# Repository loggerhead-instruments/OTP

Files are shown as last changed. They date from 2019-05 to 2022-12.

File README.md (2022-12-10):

# OTP
OpenTag Ping is an open source acoustic pinger for fish and other animals.
OTP is unique in that it incorporates an accelerometer that can be used 
to determine when an animal is vocalizing, which then triggers a coded acoustic pulse.

## Altium
PCB files for OTP tags. Each PCB project will have a PDF document containing the schematic and PCB layout. The project outputs folder contain the Gerber files needed to have the PCB manufactured.

1. OTP: Simple design with ATmega328p and LIS2DS12 accelerometer. Not recommended.
2. OTP2: Improved transmitter circuit. Not recommended.
3. OTP3: Transmitter diode changed. Not recommended.
4. OTP4: PWM moved to PD3 to take advantage of built-in PWM.
5. OTP5: Smaller board designed to match lithium battery size. Recommended.
6. OTP6: Design for custom piezoceramic where lithium battery can be placed inside piezo cylinder. Also adds pressure and depth sensor. Recommended.

## Arduino
Arduino C code for programming OTP tags. 

The accelerometer uses SPI for high speed data transfer to lower power consumption.
The accelerometer can be configured for 3 channel operation or in a special magnitude mode where the magnitude of the 3 axes is calculated on the accelerometer. Magnitude mode reduces power consumption because it reduces how much time it takes to transmit and process the accelerometer data.

OTP4 firmware works on OTP4 and OTP5

## SpecSheets
The technical specification sheets for the components used in OTP tags

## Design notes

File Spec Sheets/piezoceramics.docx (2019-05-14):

57 kHz piezoceramic ring
(https://www.steminc.com/PZT/en/piezo-ceramic-cylinder-20x17x5mm-57-khz)

Part Number: SMC20D17H5
Piezoelectric ceramic cylinder with inner and outer surface electrode for radial mode vibration.
Piezo Material: SM111 (http://www.steminc.com/piezo/PZ_property.asp)
Dimensions: Ext. Diam. 20 x Int Diam 17 x Height 5.0mm
Resonant frequency fr: 57 KHz±2 KHz
Electromechanical coupling coefficient Kr: ≥35%
Dielectric Loss tg δ: =0.5%
Resonant impedance Zm: ≤12 Ω
Static capacitance Cs: 2400pF±15%@1kHz
Test Condition: 23±3 °C 40~70% R.H.
fr, Zm, Kr => Radial mode vibration
Cs tanδ => LCR meter at 1KHz 1Vrms

70 kHz piezoceramic ring
(https://www.steminc.com/PZT/en/annular-piezo-ceramic-70-khz)

Part Number: SMC1412T4412
Annular Piezoelectric Ceramic Ø14Ø12x4mm 70 KHz. Radial mode vibration
Piezo Material: SM411 (http://www.steminc.com/piezo/PZ_property.asp)
Dimensions: OD 14 x ID 12 x Th 4mm
Resonant frequency fr: 70 KHz ± 5%
Electromechanical coupling coefficient Kr: >30%
Dielectric Loss tg δ: <2%
Static capacitance Cs: 3900pF±20%
Test Condition: 23±3 °C 40~70% R.H.
fr, Zm, Kr => Radial mode vibration
Cs tanδ => LCR meter at 1KHz 1Vrms

127 kHz piezoceramic cylinder
(https://www.steminc.com/PZT/en/piezo-ceramic-cylinder-765x65x65mm-127-khz)

Part Number: SMC7565T65111
Piezoelectric Ceramic Cylinder. Radial mode vibration
Piezo Material: SM111 (http://www.steminc.com/piezo/PZ_property.asp)
Dimensions: 7.65x6.5x6.5mm
Resonant frequency fr: 127 KHz±5KHz
Electromechanical coupling coefficient Kr:
Dielectric Loss tg δ: 1.60
Resonant impedance Zm:
Static capacitance Cs: 4000pF±15%
Test Condition: 25±3 °C 40~70% R.H.
fr, Zm, Kr => Radial mode vibration
Cs tanδ => LCR meter at 1KHz 1Vrms

155 kHz piezoceramic cylinder
(https://www.steminc.com/PZT/en/piezo-ceramic-tube-o635o49x635mm-155-khz)

Part Number: SMC0604T6121
Piezoelectric Ceramic Cylinder. Radial mode vibration
Piezo Material: SM411 (http://www.steminc.com/piezo/PZ_property.asp)
Dimensions: OD 6.35 x ID 4.9 x Th 6.35mm
Resonant frequency fr: 155 KHz ± 5%
Dielectric Loss tg δ: <2%
Resonant Impedance: <150Ω
Static capacitance Cs: 2500pF±20%
Test Condition: 23±3 °C 40~70% R.H.
fr, Zm, Kr => Radial mode vibration
Cs tanδ => LCR meter at 1KHz 1Vrms

Inductance

Resonant frequency of LC circuit given by

f= 1/(2π√(L*C))

To calculate inductance for given frequency and capacitance (units of Hertz, Farads, Henrys):

L= 1/(2πf)^2 /C

Piezoceramic Frequency | Inductance | Resonance Frequency
57 kHz | 3.2485 mH
70 kHz | 1.3255 mH | 80 kHz @ 1000 uH
127 kHz | 0.3926 mH | 127.43 kHz @ 390 uH
155 kHz | 0.4111 mH | 161.2 kHz @ 390 uH

Two inductors in series:

127 kHz piezo: 390 uH

155 kHz piezo: 390 uH + 22 uH

For 4 MHz clock, it takes 1/4 microsecond per clock cycle. We can construct the following frequencies with an integer number of clock cycles per half-cycle (so n cycles high, n cycles low):

Frequency - Clock cycles per half cycle

250.0 kHz 8 clock cycles

222.2 kHz 9 clock cycles

200 kHz 10 clock cycles

181.8 kHz 11 clock cycles

166.7 kHz 12 clock cycles

And then 153.9 kHz, 142.9 kHz, 133.3 kHz, 125 kHz, 117.7 kHz, 111.1 kHz, 105.3 kHz, 100 kHz...

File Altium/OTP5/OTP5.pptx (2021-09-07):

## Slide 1

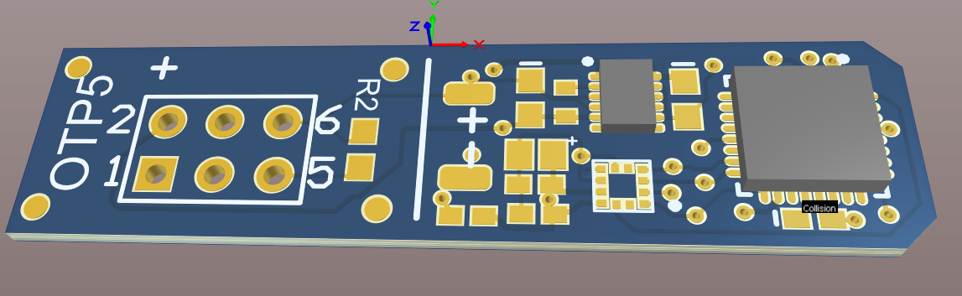
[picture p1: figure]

Battery connection

Microcontroller

Cut after programming

Accelerometer

LED

Magnetic Switch

Programming port

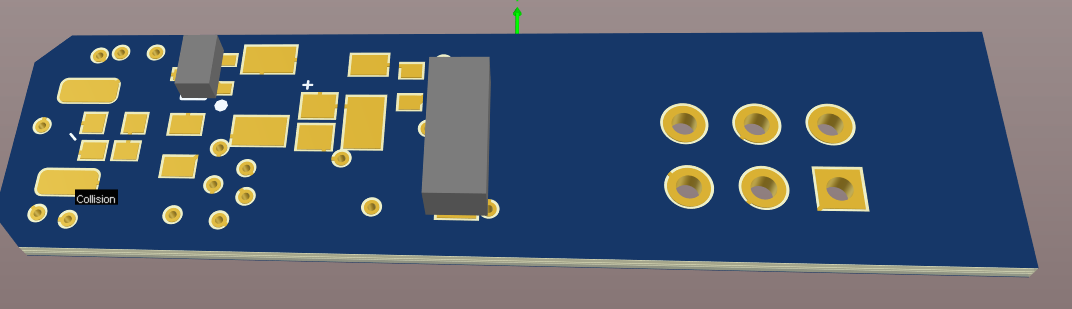
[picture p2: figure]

Piezo

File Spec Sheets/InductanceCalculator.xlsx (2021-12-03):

Frequency (Hz) | Capacitance (F) | Inductance (H) | mH | uH
57000 | 2.4e-09 | 0.003248473365 | 3.248473365 | 3248.473365
190000 | 1.65e-09 | 0.000425254695 | 0.425254695 | 425.254695
177000 | 6.35e-09 | 0.000127326853 | 0.127326853 | 127.326853
65000 | 8.5e-09 | 0.0007053336836 | 0.7053336836 | 705.3336836
30000 | 9e-09 | 0.003127197026 | 3.127197026 | 3127.197026
90000 | 5e-09 | 0.0006254394052 | 0.6254394052 | 625.4394052
127000 | 4e-09 | 0.0003926203719 | 0.3926203719 | 392.6203719
125000 | 3.5e-09 | 0.0004631825538 | 0.4631825538 | 463.1825538
66500 | 2.368e-08 | 0.0002418885297 | 0.2418885297 | 241.8885297 | custom piezo for 1/2AA battery

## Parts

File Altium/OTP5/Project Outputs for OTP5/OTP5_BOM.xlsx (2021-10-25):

Item # | Quantity | Designator | Mfg Part # | DigiKey | Comment | Description | Footprint | Type | Notes
1 | 2 | C1, C2 | C0603C106M7PAC7867 | ‎399-17780-1-ND‎ (https://www.digikey.com/product-detail/en/L0603B470KPWFT/399-17780-1-ND/8601443?itemSeq=376672183) | 10uF | Ceramic Chip Capacitor - Standard | 0603 | smt
2 | 3 | C3, C4, C6 | CC0402KPX7R8BB104 | 13-CC0402KPX7R8BB104CT-ND | 0.1uF | Ceramic Chip Capacitor - X5R, 10% | 0402 | smt
3 | 1 | C5 | F920J106MPA | 478-8115-1-ND | 10uF | Tantalum Capacitor, 20%, 6.3V or better | Tant0805 | smt
4 | 1 | C7 | F921A105MPA | 478-8122-1-ND | 47uF | Tantalum Capacitor, 20%, 6.3V or better | Tant0805 | smt
5 | 1 | D1 | HSMH-C190 | 516-1420-1-ND | LED_0603 | Red LED | Diode0603 | smt
6 | 1 | D3 | DFLS130L-7 | DFLS130LDIDKR-ND | Shottky | Schottky diode 30V 1A | DFLS130 | smt
7 | 1 | L1 | CBC3225T101MR | 587-1628-1-ND | 100uH | Fixed inductor | Inductor_NLV32T | smt
8 | 1 | L2 | MLZ1608A2R2WTD25 | 445-MLZ1608A2R2WTD25CT-ND | 2.2uH | Fixed inductor | Inductor KLZ1608AHR | smt
9 | 1 | L3 | L0603B470KPWFT | 399-17780-1-ND | 47uH | Fixed inductor | Inductor KLZ1608AHR | smt
10 | 1 | L4 | MLF2012C270KT000 | 445-1064-1-ND | 27uH | Fixed inductor | Inductor MLZ2012M220WT000 | smt
11 | 1 | Q1 | PMF250XNE | 1727-2693-1-ND | PMF250XN,115 | N-Channel Trench MOSFET, 30 V, 0.9 A, -55 to 150 degC, 3-Pin SOT323, Tape and Reel | NXP-SOT323_N | smt
12 | 1 | R1 | ERJ-PA2J103X | P17199CT-ND | 10k | ERJ-3EKF1002V 10k 5% 0603 | 2-0402 | smt
13 | 0 | R2 |  |  | omit |  | 3-0603 | DNS
14 | 1 | R3 | ERJ-2GEJ331X | P330JCT-ND | 330 | Precision Thick Film Chip Resistor, 10 Ohm to 1M Ohm Range, 1% and 0.5% Tolerance, 0402 Size, 0.063 W | 2-0402 | smt
15 | 1 | S1 | MK24-B-3-OE | 374-1137-1-ND | Reed_MK24 | SWITCH REED SPST-NC 300MA 30V | Reed MK24-B-3 | smt | Either orientation is OK. All boards should have same orientation
16 | 1 | U1 | ATMEGA328P-MU | ATMEGA328P-MU-ND | ATmega328p | 8-Bit AVR Microcontroller with 8K Bytes of In-System Programmable Flash Memory | 32M1-A_M | smt
17 | 1 | U2 | TPS62740DSSR | 296-39459-6-ND | TPS62740 | 1.8V regulator | TPS6274x | smt
18 | 1 | U3 | LIS2DS12TR | 497-16261-6-ND | LIS2DS12 | Accelerometer | LGA-12 | smt
Loggerhead Instruments
David Mann
941-266-2908
dmann@loggerhead.com

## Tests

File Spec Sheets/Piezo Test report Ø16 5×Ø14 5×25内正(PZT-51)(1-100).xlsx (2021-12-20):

Dimension： OD16.5*ID14.5*25mm |  |  |  | Material： PZT-51
Num | Radial Resonate Frequency | Anti-Resonate Frequency | Frequency Bandwidth | Status Capacitance | Dielectric Loss
 | Fs(KHz) | Fp(KHz) | Fp-Fs(Hz) | C(pf) | tg△(%)
1 | 69.89 | 88 | 18112 | 21540 | 1.8
2 | 70.14 | 88.32 | 18176 | 21340 | 1.8
3 | 69.95 | 88.48 | 18528 | 21530 | 1.8
4 | 70.14 | 87.36 | 17216 | 23680 | 1.8
5 | 70.27 | 87.84 | 17568 | 22430 | 1.8
6 | 70.21 | 88 | 17792 | 22660 | 1.8
7 | 69.84 | 88 | 18160 | 21560 | 1.8
8 | 70.02 | 88.16 | 18144 | 21690 | 1.8
9 | 69.76 | 88 | 18240 | 22010 | 1.8
10 | 69.68 | 88.16 | 18480 | 22340 | 1.8
11 | 70.21 | 88.4 | 18192 | 21090 | 1.8
12 | 70.14 | 87.36 | 17216 | 23360 | 1.8
13 | 69.95 | 88.4 | 18448 | 21330 | 1.8
14 | 70.08 | 88.16 | 18080 | 21110 | 1.8
15 | 70.02 | 88.24 | 18224 | 21730 | 1.8
16 | 70.08 | 88.32 | 18240 | 21100 | 1.8
17 | 69.68 | 87.84 | 18160 | 21990 | 1.8
18 | 69.92 | 88 | 18080 | 22650 | 1.8
19 | 70.08 | 88.64 | 18560 | 21500 | 1.8
20 | 69.76 | 88 | 18240 | 21880 | 1.8
21 | 70.21 | 87.36 | 17152 | 23060 | 1.8
22 | 69.76 | 88.16 | 18400 | 21470 | 1.8
23 | 69.76 | 88.16 | 18400 | 21330 | 1.8
24 | 69.68 | 88.32 | 18640 | 21500 | 1.8
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

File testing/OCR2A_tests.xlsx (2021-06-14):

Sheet: Prescaler=1
OCR2A | Frequency | kHz | peak-peak (V) | dB-peak' | Freq (kHz) | Notes | Setup
21 | 181818.1818 | 181.8181818 | 56 | 180.9431606 |  | bad | Reson about 2 inches from piezo
22 | 173913.0435 | 173.9130435 | 56 | 180.9431606 |  | bad | 4 MHz after prescalar
23 | 166666.6667 | 166.6666667 | 192 | 191.6454247 | 163 |  | Frequency measured from oscilloscope
24 | 160000 | 160 | 304 | 195.6368718 | 145 | nice
25 | 153846.1538 | 153.8461538 | 512 | 200.1647993 | 143 | nicer
26 | 148148.1481 | 148.1481481 | 252 | 194.0074109 | 137
27 | 142857.1429 | 142.8571429 | 528 | 200.4320785 | 140 | good
28 | 137931.0345 | 137.9310345 | 832 | 204.3818666 | 113 | excellent
29 | 133333.3333 | 133.3333333 | 320 | 196.0823997 | 130
30 | 129032.2581 | 129.0322581 | 296 | 195.4052343 | 116
31 | 125000 | 125 | 668 | 202.4749293 | 122 | v good
32 | 121212.1212 | 121.2121212 | 804 | 204.0845211 | 118 | excellent
33 | 117647.0588 | 117.6470588 | 376 | 197.483157 | 115
34 | 114285.7143 | 114.2857143 | 284 | 195.0457669 | 108
35 | 111111.1111 | 111.1111111 | 484 | 199.6763073 | 108
36 | 108108.1081 | 108.1081081 | 188 | 191.4625571 | 106
37 | 105263.1579 | 105.2631579 | 520 | 200.299467 | 103
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

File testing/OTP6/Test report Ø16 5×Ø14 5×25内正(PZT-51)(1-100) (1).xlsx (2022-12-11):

Dimension： OD16.5*ID14.5*25mm |  |  |  | Material： PZT-51
Num | Radial Resonate Frequency | Anti-Resonate Frequency | Frequency Bandwidth | Status Capacitance | Dielectric Loss
 | Fs(KHz) | Fp(KHz) | Fp-Fs(Hz) | C(pf) | tg△(%)
1 | 69.89 | 88 | 18112 | 21540 | 1.8
2 | 70.14 | 88.32 | 18176 | 21340 | 1.8
3 | 69.95 | 88.48 | 18528 | 21530 | 1.8
4 | 70.14 | 87.36 | 17216 | 23680 | 1.8
5 | 70.27 | 87.84 | 17568 | 22430 | 1.8
6 | 70.21 | 88 | 17792 | 22660 | 1.8
7 | 69.84 | 88 | 18160 | 21560 | 1.8
8 | 70.02 | 88.16 | 18144 | 21690 | 1.8
9 | 69.76 | 88 | 18240 | 22010 | 1.8
10 | 69.68 | 88.16 | 18480 | 22340 | 1.8
11 | 70.21 | 88.4 | 18192 | 21090 | 1.8
12 | 70.14 | 87.36 | 17216 | 23360 | 1.8
13 | 69.95 | 88.4 | 18448 | 21330 | 1.8
14 | 70.08 | 88.16 | 18080 | 21110 | 1.8
15 | 70.02 | 88.24 | 18224 | 21730 | 1.8
16 | 70.08 | 88.32 | 18240 | 21100 | 1.8
17 | 69.68 | 87.84 | 18160 | 21990 | 1.8
18 | 69.92 | 88 | 18080 | 22650 | 1.8
19 | 70.08 | 88.64 | 18560 | 21500 | 1.8
20 | 69.76 | 88 | 18240 | 21880 | 1.8
21 | 70.21 | 87.36 | 17152 | 23060 | 1.8
22 | 69.76 | 88.16 | 18400 | 21470 | 1.8
23 | 69.76 | 88.16 | 18400 | 21330 | 1.8
24 | 69.68 | 88.32 | 18640 | 21500 | 1.8
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

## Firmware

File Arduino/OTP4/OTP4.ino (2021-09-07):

// OpenTag Ping 
// 

// Fuses
// Extended: FF
// High: D9
// Low: E2

// baseline current no transmission: 295 uA
// baseline current  (transmitting single pulse): 330 uA
// 256 ms for pulse, 1.87 mA

#include <SPI.h>    // arduino pro/pro mini, AtMega328p 3.3V 8 MHz
#include <avr/io.h>
#include <avr/sleep.h>
#include <avr/power.h>
#include <util/delay.h>
#include <prescaler.h>
#include <avr/wdt.h>

// ID Codes
// boolean tagID[8] = {1,1,1,1,0,0,0,0};  // tag 1
boolean tagID[8] = {0,0,0,0,1,1,1,1};  // tag 2
// boolean tagID[8] = {1,1,1,1,1,1,1,1};  // tag 3
// boolean tagID[8] = {0,0,0,0,0,0,0,0};  // tag 4
// boolean tagID[8] = {1,0,0,1,1,1,0,0};  // tag 5
// boolean tagID[8] = {1,1,1,0,0,0,1,1};  // tag 6

uint8_t pulse = 0; // index into tagID - we can also use register counting with timer1 and pin5: https://forum.arduino.cc/index.php?topic=494744.0

// Detector settings
#define DET_THRESHOLD 450 // Detection threshold - 110 [mg] / 0.2441 [mg/sample]
#define DET_CRIT 8        // Critical number of detected blocks
#define DET_BLOCK 8       // Number of accelerometer samples per block

// OLD DETECTOR SETTINGS - TO DELETE
int16_t threshold = 100; // threshold for detecting signal
uint16_t thresholdCount = 100; // n values need to exceed threshold in one buffer to trigger
uint16_t bufCounter = 0; // counter for number of buffers processed. Used to control signal of tagID regardless of whether sound detected

// calculate number of bits based on tagID
//uint8_t NBIT = *(&tagID + 1) - tagID;
#define NBIT (*(&tagID + 1) - tagID)


#define LED A2
#define PWMPIN 3
#define DATAOUT 11      //MOSI
#define DATAIN 12       //MISO
#define SPICLOCK 13      //sck
#define chipSelectPinAccel 9  
#define INT1 2


// defines for setting and clearing register bits - check if we use these, switch to _BV
#ifndef cbi
#define cbi(sfr, bit) (_SFR_BYTE(sfr) &= ~_BV(bit))
#endif
#ifndef sbi
#define sbi(sfr, bit) (_SFR_BYTE(sfr) |= _BV(bit))
#endif

// default number of channels and sample rate
// can be changed by setup.txt file
// change lis2SpiFifoRead if choosing sample rate combo of 12 bit acc data
int nchan = 1;
int srate = 800;
int accelScale = 2;

// when storing magnitude of acceleraton watermark threshold are represented by 1Lsb = 3 samples
// max buffer is 256 sets of 3-axis data
#define FIFO_WATERMARK (0x80) // samples 0x0C=12 0x24=36; 0x2A=42; 0x80 = 128
#define bufLength 384 // samples: 3x watermark
int16_t accel[bufLength]; // hold up to this many samples


void setup() {
  delay(2000);
  setClockPrescaler(1); //slow down clock to run at 1.8V; makes 4 MHz clock
  pinMode(PWMPIN, OUTPUT); // output pin for OCR2B
  pinMode(LED, OUTPUT);
  digitalWrite(LED, HIGH);
  
  // initalize the  data ready and chip select pins:
  pinMode(chipSelectPinAccel, OUTPUT);
  digitalWrite(chipSelectPinAccel, HIGH);
  pinMode(SPICLOCK, OUTPUT);
  pinMode(DATAOUT, OUTPUT);
  pinMode(DATAIN, INPUT);

  // initialize watchdog timer. Remember to continuously re-initialize
  wdt_enable(WDTO_8S); // watchdog timer with 8 s timeout

  SPI.begin();
  SPI.beginTransaction(SPISettings(2000000, MSBFIRST, SPI_MODE0)); // with breadboard, speeds higher than 1MHz fail

  int testResponse = lis2SpiTestResponse();
  while (testResponse != 67) {
    delay(100);
    digitalWrite(LED, HIGH);
    delay(100);
    digitalWrite(LED, LOW);
    testResponse = lis2SpiTestResponse();
  }

  lis2SpiInit();
  digitalWrite(LED, LOW);
  wdt_reset();  

  // LED sequence for successful start: 3 medium flash
  for(int i=0; i<3; i++) {
    delay(300);
    digitalWrite(LED, HIGH);
    delay(300);
    digitalWrite(LED, LOW);
  }  
}


void loop() {
  // Process accelerometer data and look for calls
  processBuf(); // process buffer first to empty FIFO so don't miss watermark

  // Go to sleep
  wdt_reset(); // reset watchdog timer (will wake up system after 8s)
  system_sleep();

    // // supposed to sleep here, then end loop // //


//  // Regular transmissions
//  pulsePattern(1);
//
//  delay(100);
//  for(int i=0; i<5; i++){
//      digitalWrite(LED, HIGH);
//      delay(200);
//      digitalWrite(LED, LOW);
//      delay(200);
//  }
//  

     
  // 2: FSK
//  for (int j=0; j<50; j++){
//      
//    //tagID = {0,0,0,0,0,0,0,0};
//    for (int j1=8; j1<16; j1++){
//      tagID[j1] = 0;
//    }
//    
//    digitalWrite(LED, HIGH);
//    pulsePattern(1);
//    delay(200);
//    digitalWrite(LED, LOW);
//
//    //tagID = {0,0,0,0,1,1,1,1};
//    for (int j1=12; j1<16; j1++){
//      tagID[j1] = 1;
//    } 
//    pulsePattern(1);
//    delay(200);
//
//    //tagID = {1,0,1,0,1,1,1,1};
//    tagID[8] = 1;
//    tagID[10] = 1;
//    pulsePattern(1);
//    delay(300);
//
//    // Reset watchdog timer
//    wdt_reset();
//  }

}


void processBuf(){
  while((lis2SpiFifoPts() * 3 > bufLength)){
    bufCounter++;
    
    lis2SpiFifoRead(bufLength);  //samples to read
    //if(detectSound()){ 
    if(detectVocs()){ 
      digitalWrite(LED, HIGH);
      pulsePattern(1); 
      delay(100);     
    }  
    else{
    // ping after bufCounter buffers
    if(bufCounter>120){
      digitalWrite(LED, HIGH);
      pulsePattern(0);  // pulse pattern when sound not detected
      bufCounter = 0;
      delay(100);
      }
    }
  }
  digitalWrite(LED, LOW);
}

// simple algorithm to detect whether buffer contains sound
int diffData;

boolean detectVocs() {
  
  // Create variables for detector
  int dt = 0; 
  boolean blockdone = 0;
  int blockrem = 0;

  // Go through sequence
  for (int i=1; i<bufLength; i++){
    blockrem = i%DET_BLOCK; // calculate how far from new block
    if ( blockrem == 0) {
      blockdone=0; // initialize new block
    } 
    
    // check if detected
    if (blockdone==0) {
      // Calculate differential acceleration
      diffData = accel[i] - accel[i-1];      
      if (abs(diffData)>DET_THRESHOLD) {
        dt++;
        blockdone=1; // only count one detection per block
      }
    }

  }
 
  if (dt>DET_CRIT) {
    // Found a call!
    return 1;
  }
  else { 
    return 0;
  }
}

boolean detectSound(){
  // High-pass filter options:
  // diff()
  // IIR
  // FIR

  // Threshold options:
  // -fixed
  // -dynamic (e.g. 4 * SD)

  uint16_t nGtThreshold = 0;
  for (int i=1; i<bufLength; i++){
    diffData = accel[i] - accel[i-1];
    if (diffData > threshold){
      nGtThreshold += 1;
    }
  }
  if(nGtThreshold > thresholdCount) 
    return 1;
  else
    return 0;
}


void pulsePattern(boolean soundFlag){
  pulse = 0;

  // Information on timers here
  // https://www.arduino.cc/en/Tutorial/SecretsOfArduinoPWM
  // http://ww1.microchip.com/downloads/en/DeviceDoc/Atmel-7810-Automotive-Microcontrollers-ATmega328P_Datasheet.pdf

  // initialize PWM
  TCCR2B = 0; // turn off

  tagID[0] = soundFlag;
 
  // Start Timer 1 interrupt that will control changing of frequency or phase of each pulse in ping
  TCCR1A = 0;
  TCCR1B = 0;
  TCNT1 = 0;
  OCR1A = 1799;  //449 compare match register - OCR1A = 40 [cycles per bit] x (44+1) [ticks per cycle] - 1 = 1799 [for some reason, seems to be off by x2]
  TCCR1B |= (1 << WGM12); // CTC Mode
  TCCR1B |= (1 << CS10); //  no prescaler - 16-bit counter can accomodate up to 1400 cycles per bit...
  TIMSK1 |= (1 << OCIE1A); // enable timer compare interrupt

  // Do we want to sleep here until pulse is done to prevent collisions?
  
}

// Fast PWM Mode with OCRA top
// OCR2A value is the top value of the timer. So, it counts sawtooth 0 to OCR2A, 0-OCR2A, 0-OCR2A
// OCR2B value goes high until counter reaches the OCR2B value

// Ping generation for FSK mode
ISR(TIMER1_COMPA_vect){

  // check if time to turn off
  if(pulse>=NBIT){
    TCCR2A = 0; // turn off timer2 PWM
    TCCR2B = 0; // turn off PWM
    TCCR1A = 0; // turn off Timer 1
    TCCR1B = 0;
    TCNT1 = 0;
    return;
  }
  
  // FSK mode: Bit determines PWM2 pulse rate - OCR2A controls PWM period
  if(tagID[pulse]==0){
    OCR2A = 23; // 166.667 kHz (frequency, kHz = 1/ ( [OCR2A+1]/clock_speed) )
  }
  else {
    OCR2A = 25; // 24 = 160 kHz
  }
  
  // Initialize if this is first pulse
  if (pulse==0){
    OCR2B = 18;   // PWM high length, set to half of OCR2A (round down)
    TCCR2A = _BV(COM2B1) | _BV(WGM21) | _BV(WGM20);
    TCCR2B = _BV(WGM22) | _BV(CS20);  // start Fast PWM (WGM22, WGM21, WGM20 all 1); no prescaler
  }
  
  pulse++;
}


void watermark(){
  // wake up
  
}

//****************************************************************  
// set system into the sleep state 
// system wakes up when interrupt detected
void system_sleep() {
  // make all pin inputs and enable pullups to reduce power
  set_sleep_mode(SLEEP_MODE_PWR_DOWN); // sleep mode is set here
  sleep_enable();
  power_all_disable();
  attachInterrupt(digitalPinToInterrupt(INT1), watermark, LOW);
  sleep_mode();  // go to sleep
  // ...sleeping here....  
  sleep_disable();
  detachInterrupt(digitalPinToInterrupt(INT1));
  power_all_enable();
}

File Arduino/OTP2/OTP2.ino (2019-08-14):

#include <SPI.h>    // arduino pro/pro mini, AtMega 3.3V 8 MHz
#include <avr/io.h>
#include <avr/sleep.h>
#include <avr/power.h>
#include <util/delay.h>
#include <prescaler.h>

boolean tagID[32] = {0,1,0,1,0,1,0,1,0,1,0,1,0,1,0,1,0,1,0,1,0,1,0,1,0,1,0,1,0,1,0,1};
int16_t threshold = 0; // threshold for detecting signal
uint16_t thresholdCount = 100; // n values need to exceed threshold in one buffer to trigger


#define LED 4
#define PWMPIN 5
#define DATAOUT 11      //MOSI
#define DATAIN 12       //MISO
#define SPICLOCK 13      //sck
#define chipSelectPinAccel 9  
#define INT0 2
#define INT1 3
#define IR 0 // IR remote control
#define CHG 6 // charge the piezo

// pulseDelay = 3 for 400 kHz
// 19 works well for ring piezo (less ringing) determined empirically
// 11 cycles per half-cycle of a 182 kHz sine wave - at 4 MHz
// 13 cycles per half-cycle of a 154 kHz sine wave - at 4 MHz (157 kHz piezo)
// 16 cycles per half-cycle of a 125 kHz sine wave - at 4 MHz (127 kHz piezo)
// 100 is easy to hear
#define pulseDelay 26
#define offDelay 2

#define DELAY_CYCLES(n) __builtin_avr_delay_cycles(n)

// defines for setting and clearing register bits
#ifndef cbi
#define cbi(sfr, bit) (_SFR_BYTE(sfr) &= ~_BV(bit))
#endif
#ifndef sbi
#define sbi(sfr, bit) (_SFR_BYTE(sfr) |= _BV(bit))
#endif

// default number of channels and sample rate
// can be changed by setup.txt file
// change lis2SpiFifoRead if choosing sample rate combo of 12 bit acc data
int nchan = 1;
int srate = 800;
int accelScale = 2;

// when storing magnitude of acceleraton watermark threshold are represented by 1Lsb = 3 samples
// max buffer is 256 sets of 3-axis data
#define FIFO_WATERMARK (0x80) // samples 0x0C=12 0x24=36; 0x2A=42; 0x80 = 128
#define bufLength 384 // samples: 3x watermark
int16_t accel[bufLength]; // hold up to this many samples


void setup() {
  setClockPrescaler(1); //slow down clock to save battery 4 = 16x slower // makes 4 MHz clock
  pinMode(PWMPIN, OUTPUT); // output pin for OCR0B
  pinMode(CHG, OUTPUT);
  pinMode(LED, OUTPUT);
  pinMode(IR, INPUT);

  digitalWrite(CHG, LOW);


//// https://www.eprojectszone.com/how-to-modify-the-pwm-frequency-on-the-arduino-part1/
//TCCR0A=0;//reset the register
//TCCR0B=0;//reset tthe register
//TCCR0A=0b00110011;// fast pwm mode on pin 5 (COM0B1)
////TCCR0B=0b00000010;// prescaler 8
//TCCR0B=0b00001001;// no prescaler; WGM02 is 1 (toggle Oc0A on Compare Match)
//OCR0A=72; // 4 MHz/72 = 55.5 kHz
////OCR0A=255;  // 4 MHz/255 (largest value because 8-bit timer) = 15.6 kHz
  
  
  // initalize the  data ready and chip select pins:
  pinMode(chipSelectPinAccel, OUTPUT);
  digitalWrite(chipSelectPinAccel, HIGH);
  pinMode(SPICLOCK, OUTPUT);
  pinMode(DATAOUT, OUTPUT);
  pinMode(DATAIN, INPUT);

  SPI.begin();
  SPI.beginTransaction(SPISettings(2000000, MSBFIRST, SPI_MODE0)); // with breadboard, speeds higher than 1MHz fail

  int testResponse = lis2SpiTestResponse();
  while (testResponse != 67) {
    delay(100);
    digitalWrite(LED, HIGH);
    delay(100);
    digitalWrite(LED, LOW);
    testResponse = lis2SpiTestResponse();
  }

  lis2SpiInit();
  
}


void loop() {
     //processBuf(); // process buffer first to empty FIFO so don't miss watermark
     //system_sleep();

     pulseOut();
     delay(100);
     
     // ... ASLEEP HERE...
}


void processBuf(){
  while((lis2SpiFifoPts() * 3 > bufLength)){
    lis2SpiFifoRead(bufLength);  //samples to read
    if(detectSound()){
      digitalWrite(LED, HIGH);
     // pulsePattern();
      pulseOut();
    }  
  }
  digitalWrite(LED, LOW);
}


// simple algorithm to detect whether buffer contains sound
int diffData;

boolean detectSound(){
  // High-pass filter options:
  // diff()
  // IIR
  // FIR

  // Threshold options:
  // -fixed
  // -dynamic (e.g. 4 * SD)

  uint16_t nGtThreshold = 0;
  for (int i=1; i<bufLength; i++){
    diffData = accel[i] - accel[i-1];
    if (diffData > threshold){
      nGtThreshold += 1;
    }
  }
  if(nGtThreshold > thresholdCount) 
    return 1;
  else
    return 0;
}

void pulsePattern(){
  // 32-bit code
  for(int i=0; i<32; i++){
    pulseOut();
    for(int k=0; k<2*(tagID[i]+1); k++){
       DELAY_CYCLES(100);
    }
  }
}

void pulseOut(){
  // PWM
  // when tried this got random bursts 
//  TCCR0A=0;//reset the register
//  TCCR0B=0;//reset the register
//  TCCR0A=0b00110011;// fast pwm mode on pin 5 (COM0B1)
//  TCCR0B=0b00001001;// no prescaler; WGM02 is 1 (toggle Oc0A on Compare Match)
//  OCR0A=23; // 4 MHz/72 = 55.5 kHz; 4 MHz/23 = 173.9 kHz
//
//  DELAY_CYCLES(20);
//
//  TCCR0A=0;//reset the register
//  TCCR0B=0;//reset the register

  
  
// CHG
// This does not seem to have any effect on output level
//    sbi(PORTD, CHG);
//    DELAY_CYCLES(2000);
//    cbi(PORTD, CHG);


  // when use loop, get extra delay
  // amplitude is higher when pulseDelay is longer
  // amplitude is highest when offDelay is 0 (up to 40V)
  
    sbi(PORTD, PWMPIN);
    DELAY_CYCLES(pulseDelay);
    cbi(PORTD, PWMPIN);
    DELAY_CYCLES(offDelay);

    sbi(PORTD, PWMPIN);
    DELAY_CYCLES(pulseDelay);
    cbi(PORTD, PWMPIN);
    DELAY_CYCLES(offDelay);
      
    sbi(PORTD, PWMPIN);
    DELAY_CYCLES(pulseDelay);
    cbi(PORTD, PWMPIN);
    DELAY_CYCLES(offDelay);

    sbi(PORTD, PWMPIN);
    DELAY_CYCLES(pulseDelay);
    cbi(PORTD, PWMPIN);
    DELAY_CYCLES(offDelay);
      
    sbi(PORTD, PWMPIN);
    DELAY_CYCLES(pulseDelay);
    cbi(PORTD, PWMPIN);
    DELAY_CYCLES(offDelay);

    sbi(PORTD, PWMPIN);
    DELAY_CYCLES(pulseDelay);
    cbi(PORTD, PWMPIN);
    DELAY_CYCLES(offDelay);
      
    sbi(PORTD, PWMPIN);
    DELAY_CYCLES(pulseDelay);
    cbi(PORTD, PWMPIN);
    DELAY_CYCLES(offDelay);

    sbi(PORTD, PWMPIN);
    DELAY_CYCLES(pulseDelay);
    cbi(PORTD, PWMPIN);
    DELAY_CYCLES(offDelay);
}

void watermark(){
  // wake up
  
}
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

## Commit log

2018-10-09 OTP schematic and PCB
    [OTP.PcbDoc, OTP.PrjPCB, OTP.SchDoc]
2018-10-09 fiducials and V on uC programmer to 1.8V
    [OTP.PcbDoc, OTP.SchDoc]
2018-11-01 trigger based on a number of samples above threshold
2019-03-15 spec sheet folder
    [OTP.PcbDoc]
2019-03-15 OTP pick and place and PDF
    [OTP.PrjPCB, Pick Place for OTP.csv]
2019-03-15 OTP2 intiial commit
    [OTP2.PrjPCB, OTP2.SchDoc]
2019-04-02 OTP2 schematic
    [OTP2.PcbDoc, OTP2.PrjPCB, OTP2.SchDoc]
2019-04-02 PCB routing
    [OTP2.PcbDoc, OTP2.SchDoc]
2019-04-02 final routing
    [OTP2.PcbDoc, OTP2.PrjPCB]
2019-04-22 OTP2 PCB
    [OTP2.PcbDoc, OTP2.SchDoc, Pick Place for OTP2.csv]
2019-05-14 OTP3 PCB
    [OTP3.PcbDoc, OTP3.PrjPCB, OTP3.SchDoc]
2019-05-14 add silkscreen
    [OTP3.PcbDoc, OTP3.PrjPCB]
2019-05-15 add mosfet spec
    [OTP.PrjPCB, OTP3.PrjPCB]
2019-07-19 pulse out test
    [InductanceCalculator.xlsx, OTP3.SchDoc, Pick Place for OTP3.csv]
2019-08-12 OTP4 PCB
    [OTP4.PcbDoc, OTP4.PrjPCB, OTP4.SchDoc]
2019-08-12 OTP3 pick and palce
    [Pick Place for OTP3.csv]
2019-08-14 move traces away from edge
    [OTP4.PcbDoc]
2019-08-15 panel from pcbway
2019-09-13 OTP4.1 PWM pin change
    Change PWM to Pin 1 which is connected to Timer 2
    Moved interrupt2 from accelerometer
    [OTP4.PcbDoc, OTP4.SchDoc]
2019-11-12 OTP4 altium
    [OTP4.PcbDoc, OTP4.SchDoc, Pick Place for OTP4.csv]
2019-11-12 OTP4 arduino
2019-11-27 PWM with Timer1 controlling frequency change
    [OTP4.PrjPCB]
2020-02-03 Modified start LED
2020-04-24 Temporary update pinger code
    Single-pulse transmission code
    -Fixed interrupt-based transmissions
    -Fixed high current draw and component overheating
    -Corrected frequency and bit-length
2021-04-16 fix extra length pulse at end
    [OCR2A_frequency.xlsx]
2021-06-14 empirically tested OCR2A rates
    [OCR2A_tests.xlsx]
2021-07-26 make detections visible with LED
2021-07-26 power consumption measurements
2021-09-07 spec sheets
    [InductanceCalculator.xlsx]
2021-09-07 ppt overview
    [OTP5.PrjPCB]
2021-09-08 rearrange tall components on back
    [OTP5.PcbDoc]
2021-10-25 altium otp5
    [OTP5.GBL, OTP5.GBO, OTP5.GBP, OTP5.GBS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]
2021-12-04 adjust for piezo thickness
    [OTP6.PcbDoc]
2021-12-04 avoid collision with inside of piezo
    [OTP6.PcbDoc]
2021-12-04 adjust piezo connections
    [OTP6.PcbDoc]
2021-12-04 fix silkscreen
    [OTP6.PcbDoc]
2021-12-04 clean up routing
    [OTP6.PcbDoc]
2021-12-08 PCBWay production
    [W20819ASU206 EQ.xls]
2021-12-20 Create Piezo Test report Ø16 5×Ø14 5×25内正(PZT-51)(1-100).xlsx
    [Piezo Test report Ø16 5×Ø14 5×25内正(PZT-51)(1-100).xlsx]
2022-01-14 remove fiducials
    could short piezo
    [OTP6.PcbDoc, OTP6.PrjPCB, OTP6.SchDoc, Pick Place for OTP6.csv]
2022-02-15 sample LS1 recording of OTP6
2022-12-10 PDF of schematic and PCBs
    [OTP4.PrjPCB, OTP5.PrjPCB, OTP6.PrjPCB]
2022-12-11 OTP6 piezo info
    [Test report Ø16 5×Ø14 5×25内正(PZT-51)(1-100) (1).xlsx]
